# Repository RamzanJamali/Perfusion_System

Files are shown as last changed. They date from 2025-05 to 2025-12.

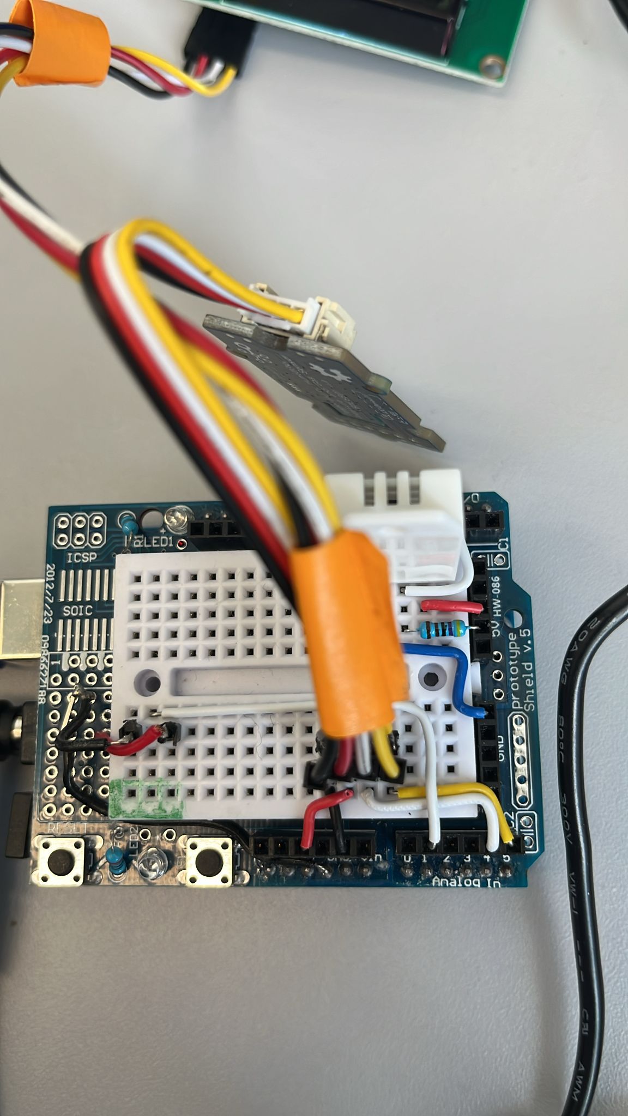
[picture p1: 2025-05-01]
Materials/SensorSetup.jpeg

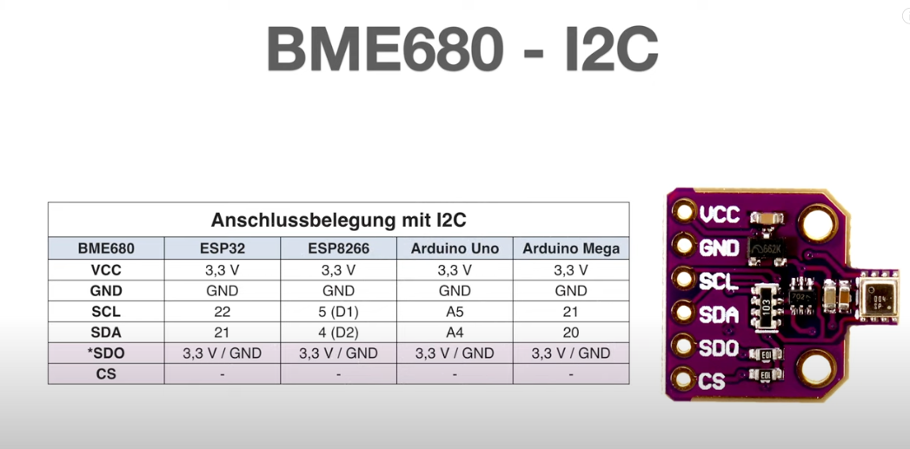
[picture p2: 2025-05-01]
Materials/Specs/BME680_I2C_specs.png

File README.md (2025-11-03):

# Pressure-Controlled Perfusion System

A modular, open-source pressure-controlled perfusion system designed for the biomechanical characterization of corneal tissue. This system provides precise control over retrocorneal pressure and perfusion flow rate for *ex vivo* experiments.

## 🚀 Quick Start

1.  **Hardware:** Assemble the mechanical components and connect the electronics as per the `hardware/` documentation.
2.  **Firmware:** Flash the Arduino with the appropriate controller firmware from the `Controller/` directory.
3.  **Software:** Install Python dependencies and run the recommended dashboard.
    ```bash
    pip install -r software/Dashboard_2/requirements.txt
    python software/Dashboard_2/app.py
    ```

## 📁 Repository Structure & Component Guide

Here is a breakdown of the key software components and their intended use:

| Component | Purpose | Recommendation |
| :--- | :--- | :--- |
| **`Controller/Controller_1`** | Firmware configured for the **Variohm CIT3100** pressure sensor. | Use if your hardware uses the CIT3100 sensor. |
| **`Controller/Controller_2`** | Firmware configured for the **Ceraphant PTC31B** pressure sensor. | **Recommended** for systems with the PTC31B sensor. |
| **`software/Dashboard_1`** | Legacy version of the Python control dashboard. | For reference or specific use cases. |
| **`software/Dashboard_2`** | Enhanced version with improved data visualization and control. | **Recommended** for all new installations. |

### 🔧 Hardware Specifications

Key components used in this system include:

*   **Stepper Motor Driver:** The TMC2209 driver module controls the NEMA 17 stepper motor, providing silent operation and advanced features like stealthChop2 for noiseless motion and spreadCycle for high-speed performance.
*   **Pressure Transducer:** The Ceraphant PTC31B is a pressure switch with a ceramic, vacuum-tight measuring cell, used for safe monitoring of absolute and gauge pressure. It is suitable for measurements in gases, vapors, and liquids.

## ⚙️ How to Use This Repository

### Downloading the Project

To get a copy of the project, you can **clone** the repository or **download it as a ZIP** file.

*   **Clone (recommended for development):**
    ```bash
    git clone https://github.com/RamzanJamali/Perfusion_System.git
    ```
*   **Download ZIP:**
    Click the `Code` button on the GitHub repository page and select "Download ZIP".

### Navigating the Code

- The `Controller/` directory contains the Arduino firmware. Select the version that matches your pressure sensor.
- The `software/` directory contains the Python-based dashboards. Use `Dashboard_2` for the best experience.
- Refer to the `hardware/` directory for assembly guides, CAD files, and the bill of materials.

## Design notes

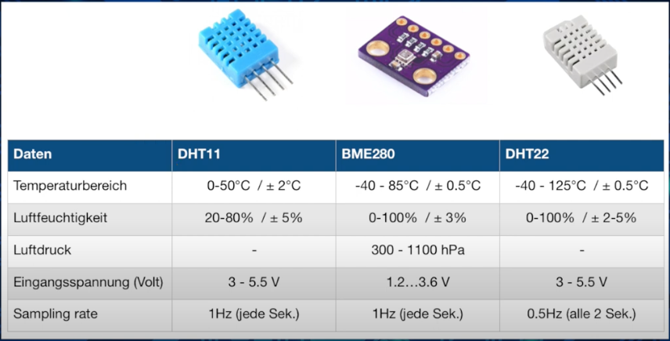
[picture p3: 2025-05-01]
Materials/Specs/DHT_specs.png

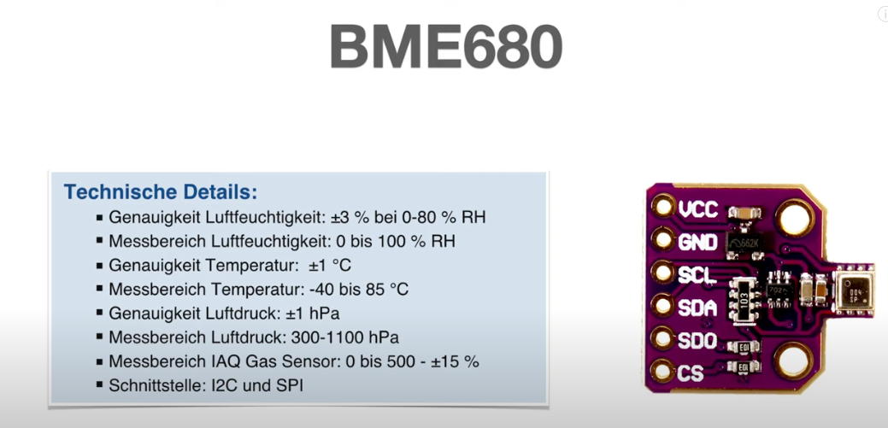
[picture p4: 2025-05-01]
Materials/Specs/BME680_specs.png

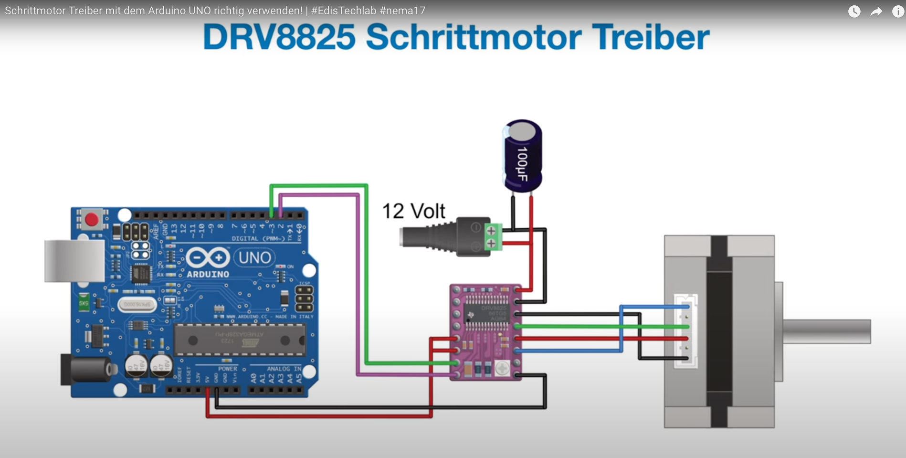
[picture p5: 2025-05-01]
Materials/Specs/DRV8825_motor_circuit.png

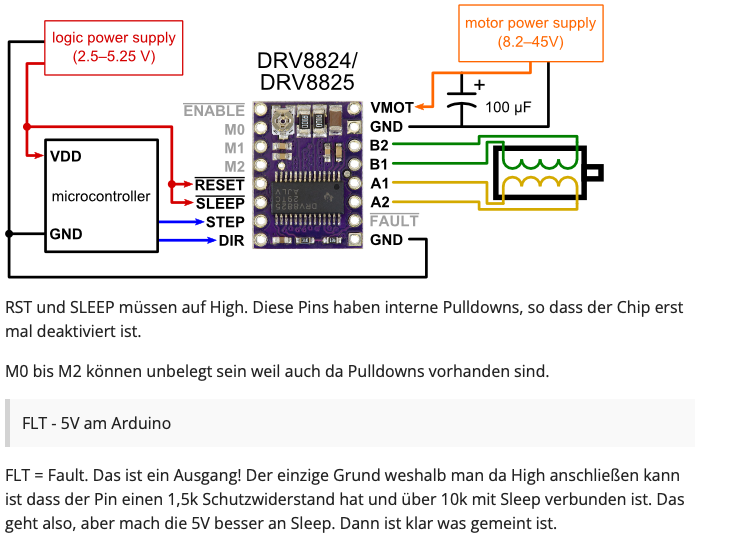
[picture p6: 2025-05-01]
Materials/Specs/DRV8825_circuit.png

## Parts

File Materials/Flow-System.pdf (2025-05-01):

## Etablierung eines druckkontrollierten

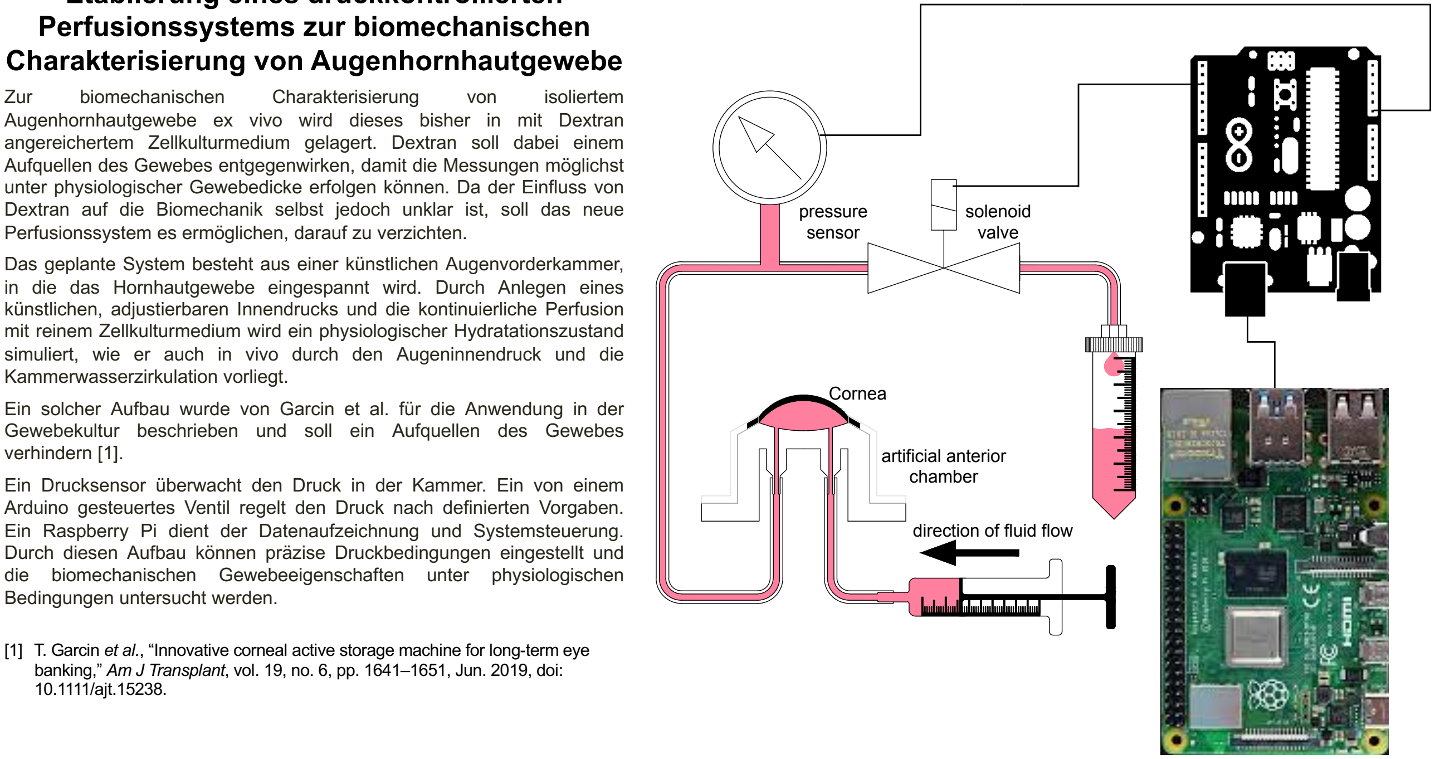
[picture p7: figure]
Perfusionssystems zur biomechanischen; Zur; biomechanischen; Charakterisierung; von; isoliertem; Kammerwasserzirkulation vorliegt.; verhindern [1].; die biomechanischen Gewebeeigenschaften unter physiologischen Bedingungen untersucht werden.; 10.1111/ajt.15238.; solenoid valve; pressure sensor; Cornea; artificial anterior chamber; direction of fluid flow

## Charakterisierung von Augenhornhautgewebe

Augenhornhautgewebe ex vivo wird dieses bisher in mit Dextran angereichertem Zellkulturmedium gelagert. Dextran soll dabei einem Aufquellen des Gewebes entgegenwirken, damit die Messungen möglichst unter physiologischer Gewebedicke erfolgen können. Da der Einfluss von Dextran auf die Biomechanik selbst jedoch unklar ist, soll das neue Perfusionssystem es ermöglichen, darauf zu verzichten.
Das geplante System besteht aus einer künstlichen Augenvorderkammer, in die das Hornhautgewebe eingespannt wird. Durch Anlegen eines künstlichen, adjustierbaren Innendrucks und die kontinuierliche Perfusion mit reinem Zellkulturmedium wird ein physiologischer Hydratationszustand simuliert, wie er auch in vivo durch den Augeninnendruck und die

Ein solcher Aufbau wurde von Garcin et al. für die Anwendung in der Gewebekultur beschrieben und soll ein Aufquellen des Gewebes

Ein Drucksensor überwacht den Druck in der Kammer. Ein von einem Arduino gesteuertes Ventil regelt den Druck nach definierten Vorgaben. Ein Raspberry Pi dient der Datenaufzeichnung und Systemsteuerung. Durch diesen Aufbau können präzise Druckbedingungen eingestellt und

[1] T. Garcin et al., “Innovative corneal active storage machine for long-term eye banking,” Am J Transplant, vol. 19, no. 6, pp. 1641–1651, Jun. 2019, doi:

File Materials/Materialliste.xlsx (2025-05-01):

Bauteil | Link | Bemerkung | Notiz
Netzteil
VOLTCRAFT VC-12878460 Steckernetzteil, Festspannung 24 V/DC 2.5 A 60 W | Conrad (https://www.conrad.de/de/p/voltcraft-vc-12878460-steckernetzteil-festspannung-24-v-dc-2-5-a-60-w-2575692.html) | 60 Watt
Schrittmotortreiber
Doppel H-Brücke DC Motor Controller Board Modul AZ-L298N | AZ-Delivery (https://www.az-delivery.de/products/dual-h-bridge-dc-motor-controller?gad_source=5) |  | Motor Spannung 5-35V / Logik Spannung 5-7V / Leistung 25 Watt / Maximalstrom pro Phase 4A / Dauerstrom pro Phase 2 A / 4 Phasen | Ich tendiere zum DRV 8825 habe allerdings keine Erfahrungen mit solchen Modulen und bin für Ratschläge dankbar
DRV8825 Schrittmotor-Treiber-Modul | AZ-Delivery (https://www.az-delivery.de/products/drv8825-schrittmotor-treiber-modul-mit-kuhlkorper?variant=37100118866&gad_source=5) | 5er set | Motor Spannung 8.2-45V / Logik Spannung intern 3.3V / Maximalstrom pro Phase 2,5A / Dauerstrom pro Phase 1 A / Schritte: Voll, 1/2, 1/4, 1/8, 1,16, und 1/32 / 4 Phasen
Sensoren
DHT22 AM2302 Temperatursensor und Luftfeuchtigkeitssensor | AZ-Delivery (https://www.az-delivery.de/products/dht22?_pos=1&_sid=f178b3009&_ss=r)
101020513 - BME680 Temperatur-, Feuchtigkeits- und Drucksensor für Arduino | Distrelec (https://www.distrelec.de/de/bme680-temperatur-feuchtigkeits-und-drucksensor-fuer-arduino-seeed-studio-101020513/p/30121569?ext_cid=gpgooaqdede-Search-DSACatch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)
Variohm CIT3100-G-00004-B-4-A | Variohm (https://www.variohm.de/produkte/drucksensoren-und-druckschalter/drucksensoren/cit3100-niederdrucksensoren)
Ceraphant PTC31B-AAAM1CGBWBJA | Endress & Hauser (https://www.de.endress.com/de/messgeraete-fuer-die-prozesstechnik/druck/Absolut-Relativ-Ceraphant-PTC31B?t.tabId=product-configure)
Schrittmotor:
Joy-it Schrittmotor NEMA17-06 neu 0.59 Nm 2 A 2 A Wellen-Durchmesser: 5 mm | Conrad (https://www.conrad.de/de/p/joy-it-schrittmotor-nema17-06-neu-0-59-nm-2-a-2-a-wellen-durchmesser-5-mm-2355876.html)
Sonstiges
MB102 Breadboard Netzteil Adapter Power Supply Modul 3.3V/5V | AZ-Delivery (https://www.az-delivery.de/products/mb102-breadboard?_pos=45&_sid=0396cc324&_ss=r) | 3er Set | Prototyping Adapter um die Schaltungen zu testen könnte gut sein um die Schrittmotorschaltung anfangs zu testen
ElKo Sortiment Elektrolytkondensator Aluminium 24 Varianten, 500 Stück 0.1uF – 1000uF | AZ-Delivery (https://www.az-delivery.de/products/elko-sortiment-mit-500-stuck-elektrolytkondensatoren-0-1-f-1000-f) |  | Für den Betrieb eines DRV 8825 wird ein Kondensator (100 µF) benötigt
Prototyping Prototype Shield Mini Breadboard für UNO R3 | AZ-Delivery (https://www.az-delivery.de/products/prototyping-shield?variant=6127218851867) | 5er Set
1-Relais 5V KY-019 Modul High-Level-Trigger | AZ-Delivery (https://www.az-delivery.de/products/relais-modul?variant=8138392109152) | 5er Set | Steuerung des Magnetventiels (Stomschalter)
Hochpräzises Strom-zu-Spannungswandler Modul, 4-20mA auf 0-5V Signalumwandlungsmodul I/V-Wandler Analogausgang Platine | Amazon (https://www.amazon.de/Strom-zu-Spannungswandler-Signalumwandlungsmodul-Konverter-Analogausgang-Board/dp/B07XNPLQ3K?__mk_de_DE=ÅMÅŽÕÑ&nsdOptOutParam=true&s=ce-de) |  | Amazon wurde von meinem Endress und Hauser Kontakt empfohlen fruugo ist günstiger aber auch anders und eventuell komplizierter zum Einstellen
Current To Voltage Module 0/4-20mA To 0-3.3V 5V 10V Voltage Transmitter | fruugo (https://www.fruugo.de/strom-zu-spannungs-modul-04-20ma-bis-0-33v-5v-10v-spannungstransmitter/p-274529440-609483705?language=de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)
LCD Display
HD44780 2004 LCD Display Bundle 4x20 Zeichen mit I2C Schnittstelle | AZ-Delivery (https://www.az-delivery.de/products/hd44780-2004-lcd-display-bundle-4x20-zeichen-mit-i2c-schnittstelle?variant=13538165915744) | 3er Set | Sind noch zwei in Freiburg vorrätig
Mechanische Bauteile
Wellenkupplung RB flexibel D18L25 5,00/6,35mm | dold (https://www.dold-mechatronik.de/Wellenkupplung-RB-flexibel-D18L25-500-635mm)
Linearlager 8mm LM8UUAJ, einstellbar | dold (https://www.dold-mechatronik.de/Linearlager-8mm-LM8UUAJ-einstellbar)
Präzisionswelle 8mm h6, geschliffen und gehärtet, Edelstahl X46Cr13 (1.4034), 0,4kg/m, Zuschnitt 50-3000mm | dold (https://www.dold-mechatronik.de/Praezisionswelle-8mm-h6-geschliffen-und-gehaertet-Edelstahl-X46Cr13-Zuschnitt) | 2 x 1000 mm
1 Gewindestange M8x1000 mm - Edelstahl A4 - DIN 976 | BefestigungsFuchs (https://www.befestigungsfuchs.de/eisenwaren/gewindestangen-gewindestuecke/edelstahl/1-gewindestange-m8x1000-mm-edelstahl-a4-din-976) | 2 x 1000 mm
40tlg Muttern/Unterlegscheiben Set für M8 Gewindestangen Edelstahl A4 | BefestigungsFuchs (https://www.befestigungsfuchs.de/eisenwaren/gewindestangen-gewindestuecke/edelstahl/40tlg-muttern-unterlegscheiben-set-fuer-m8-gewindestangen-edelstahl-a4)
1 Zylinderschraube M3x14mm - Innensechskant - Edelstahl A4 - DIN 7984 | BefestigungsFuchs (https://www.befestigungsfuchs.de/schrauben/zylinderschrauben/innensechskant/1-zylinderschraube-m3x14mm-innensechskant-edelstahl-a4-din-7984) | 40 Stk bestellen für Mengenrabatt
1 Sechskantmutter - M3 - SW5.5 - Edelstahl A4-50 - DIN 934 | BefestigungsFuchs (https://www.befestigungsfuchs.de/eisenwaren/muttern/sechskantmuttern/1-sechskantmutter-m3-sw5.5-edelstahl-a4-50-din-934) | 20 Stk bestellen für Mengenrabatt
1 Unterlegscheibe DIN 125 Form A - für M3 - Aussen-Ø=7mm - Edelstahl A2 | BefestigungsFuchs (https://www.befestigungsfuchs.de/eisenwaren/unterlegscheiben-ringe/1-unterlegscheibe-din-125-form-a-fuer-m3-aussen-oe-7mm-edelstahl-a2) | 20 Stk bestellen für Mengenrabatt
500 Innensechskantschrauben mit Teilgewinde DIN 912 Edelstahl A4 5x8mm | Befestigungsfuchs (https://www.befestigungsfuchs.de/schrauben/zylinderschrauben/innensechskant/500-innensechskantschrauben-mit-teilgewinde-din-912-edelstahl-a4-5x8mm)
0.0.448.07 -- / -- Profil 5 20x40 natur 3.000mm | ITEM (https://www.item24.com/de-de/profil-5-40x20-natur-44807?supplyUnit=STUECK&nominalLength=3000&nuten=-1&category=profiltechnik)

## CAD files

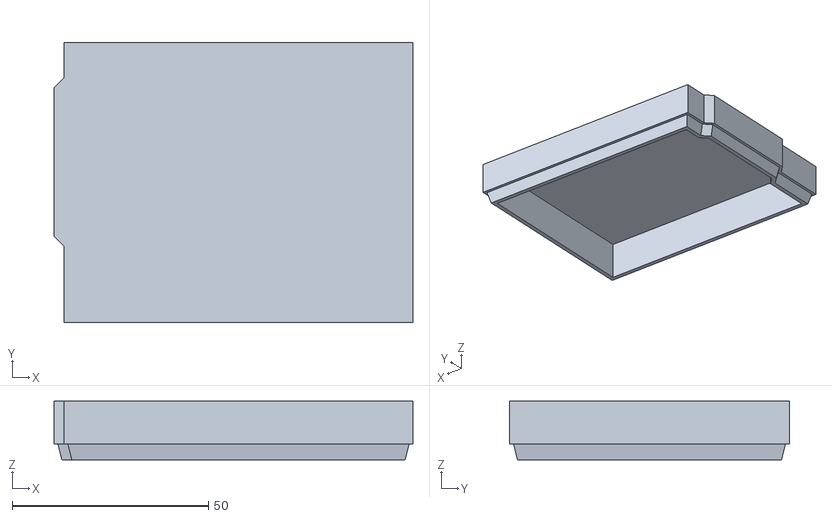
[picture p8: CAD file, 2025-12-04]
3D files/Arduino_Housing Top v2.stl
91.6 x 71.3 x 15.0

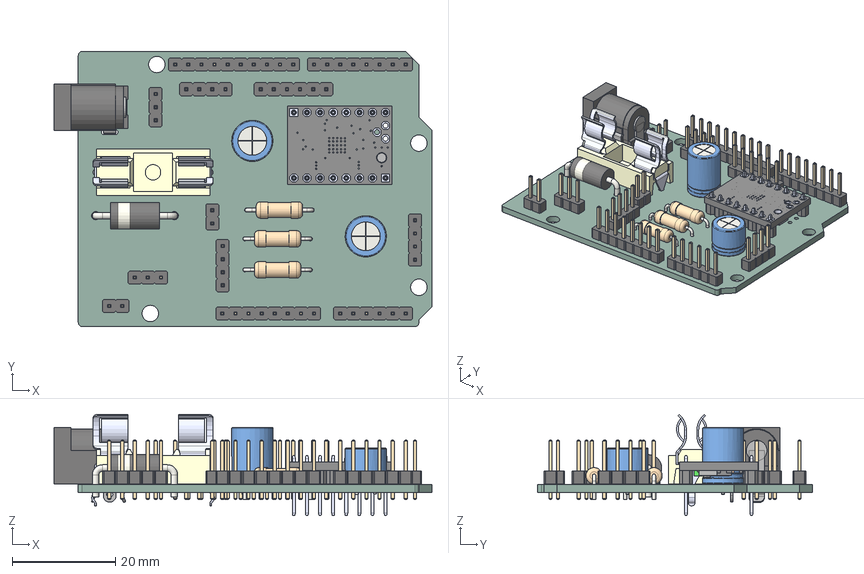
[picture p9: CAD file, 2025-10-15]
Perfusion_Shield/Perfusion_Shield.step
73.3 x 53.3 x 19.6 mm
PinHeader_1x08_P2.54mm_Vertical x 2
PinHeader_1x06_P2.54mm_Vertical x 2
PinHeader_1x10_P2.54mm_Vertical
PinHeader_1x03_P2.54mm_Vertical x 2
MC000827
PinHeader_1x04_P2.54mm_Vertical x 3
R_Axial_DIN0309_L9.0mm_D3.2mm_P12.70mm_Horizontal x 3
PinHeader_1x02_P2.54mm_Vertical x 2
C_Radial_D8.0mm_H7.0mm_P3.50mm
BarrelJack_GCT_DCJ200-10-A_Horizontal
D_DO-201AD_P15.24mm_Horizontal
TMC2209SILENTSTEPSTICK--3DModel-STEP-269445
C_Radial_D8.0mm_H11.5mm_P3.50mm
Perfusion_Shield_PCB

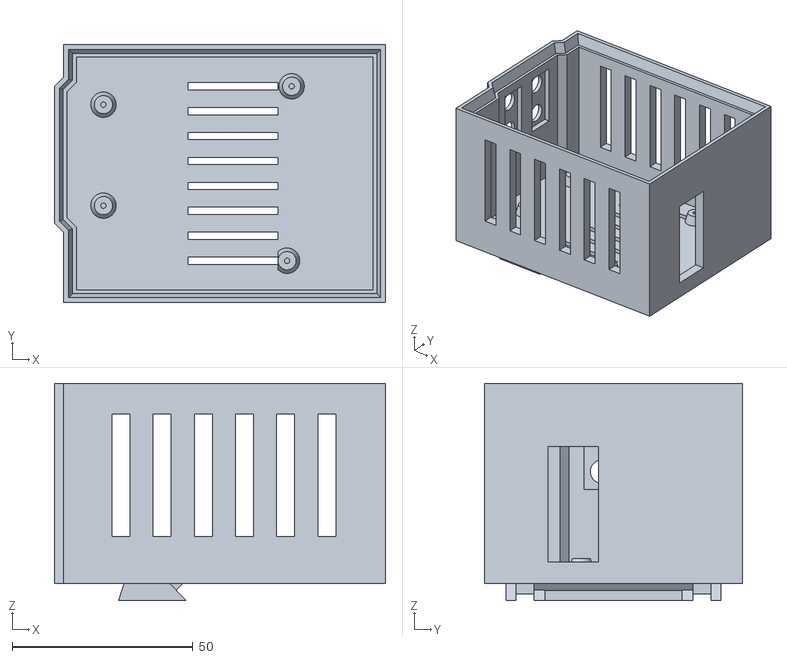
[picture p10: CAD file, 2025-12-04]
3D files/Arduino_Housing v5.stl
91.6 x 71.3 x 60.1

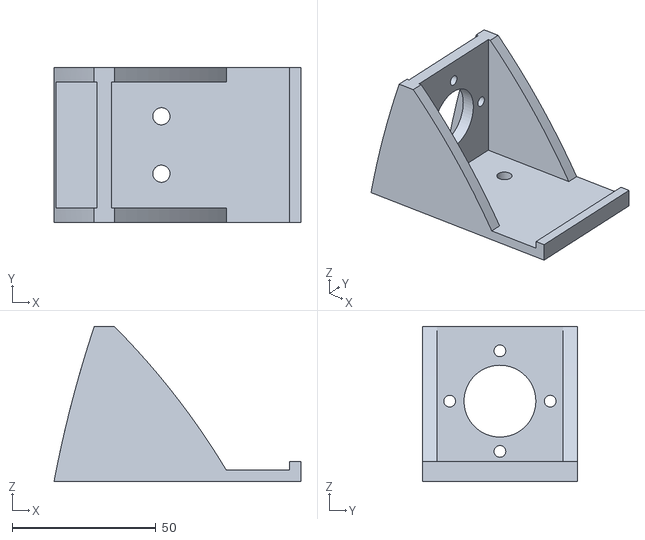
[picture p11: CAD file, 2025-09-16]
3D files/MGL17-G20_Holder v1.stl
86.0 x 54.0 x 54.0

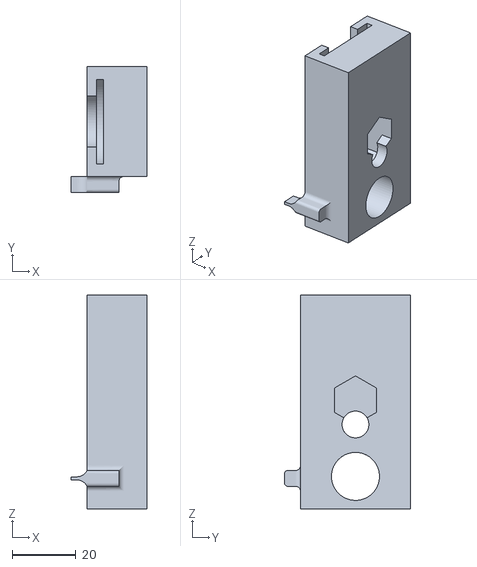
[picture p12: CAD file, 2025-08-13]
3D files/Plunger v15.stl
23.8 x 39.5 x 67.1

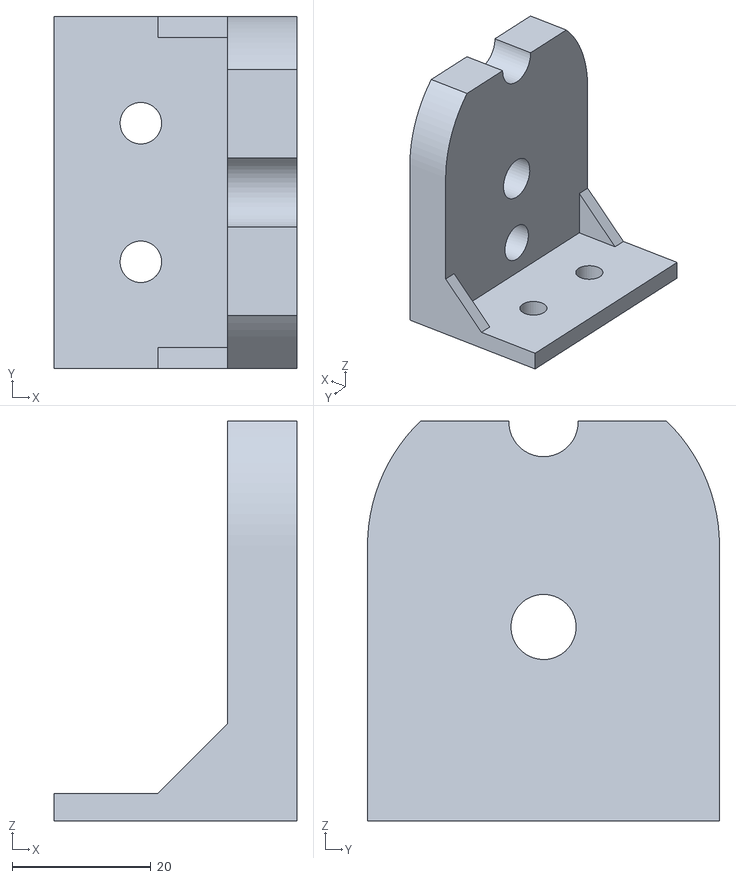
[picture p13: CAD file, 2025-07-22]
3D files/Syringe_10ml v7.stl
35.0 x 50.8 x 57.7

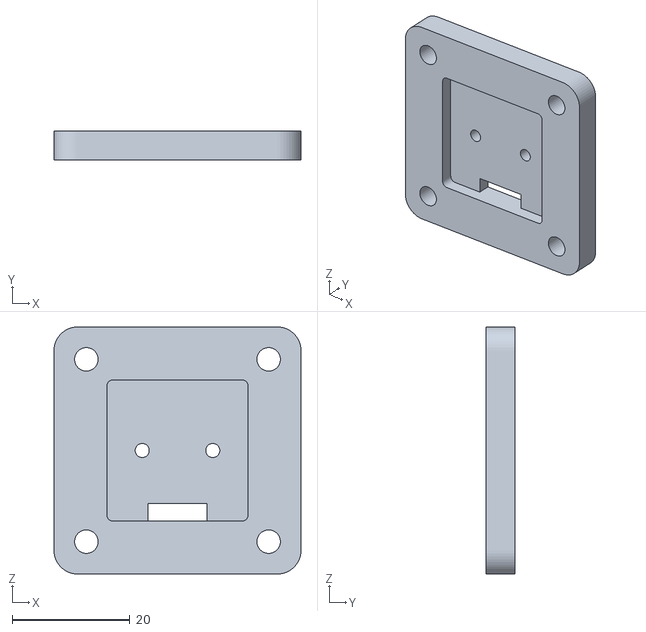
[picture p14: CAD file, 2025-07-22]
3D files/AS5048A_mount v2.stl
42.0 x 5.00 x 42.0

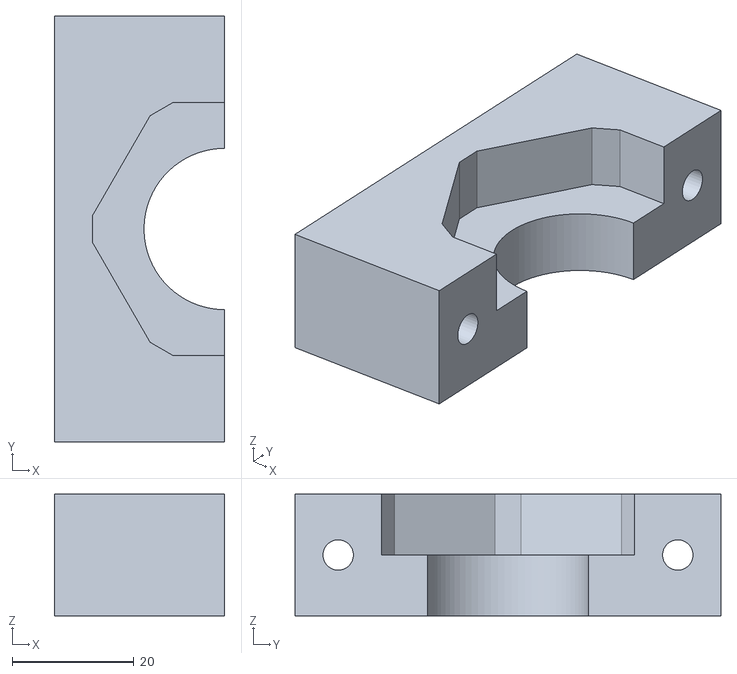
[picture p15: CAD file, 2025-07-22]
3D files/Pressure_Sensor_Holder v3.stl
28.0 x 70.0 x 20.0

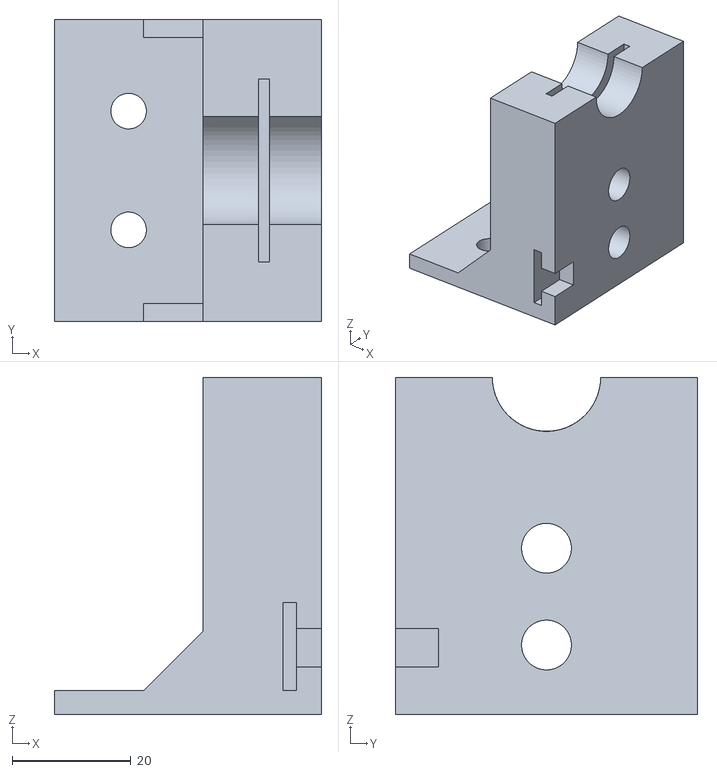
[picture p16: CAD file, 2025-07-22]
3D files/Barrel 10ml with IR Button v3.stl
45.0 x 50.8 x 56.8

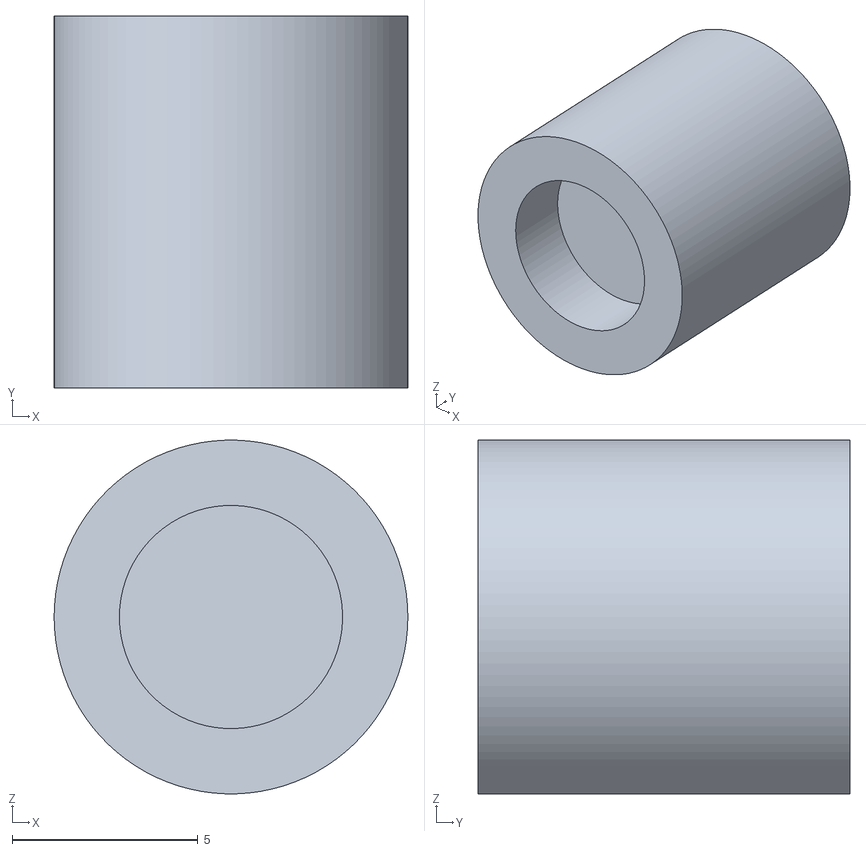
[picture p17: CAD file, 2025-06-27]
3D files/Magnet_holder v2.stl
9.51 x 10.0 x 9.50

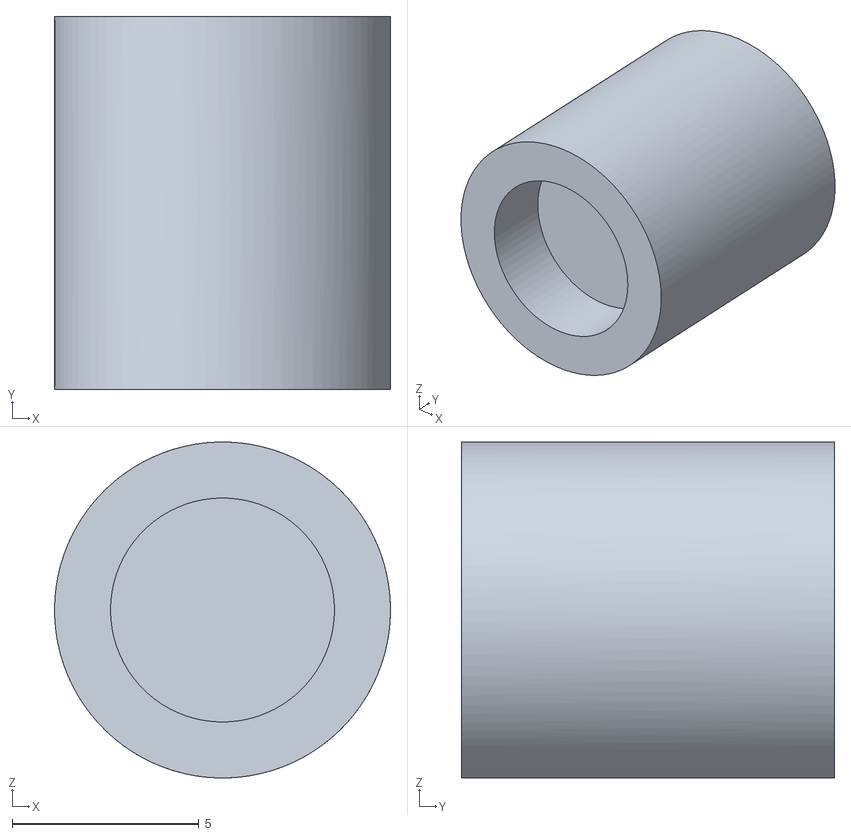
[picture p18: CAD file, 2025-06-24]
3D files/Magnet_holder v1.stl
9.00 x 10.0 x 9.00

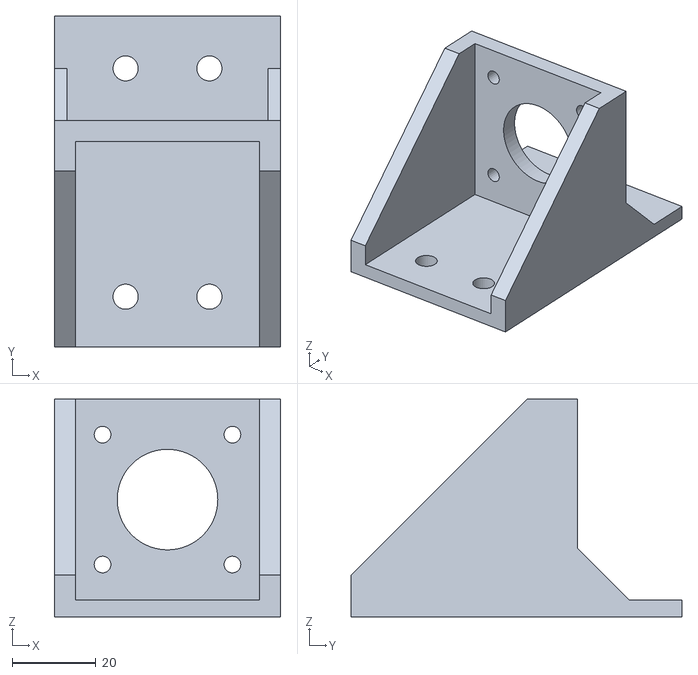
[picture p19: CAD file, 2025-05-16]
3D files/NemaMount 2 v3.stl
54.0 x 79.0 x 52.0

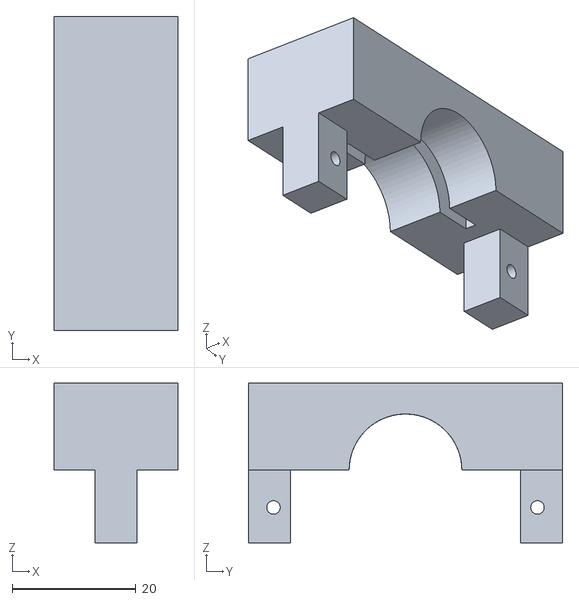
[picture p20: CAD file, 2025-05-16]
3D files/Barrel_head.stl
20.0 x 50.8 x 25.9

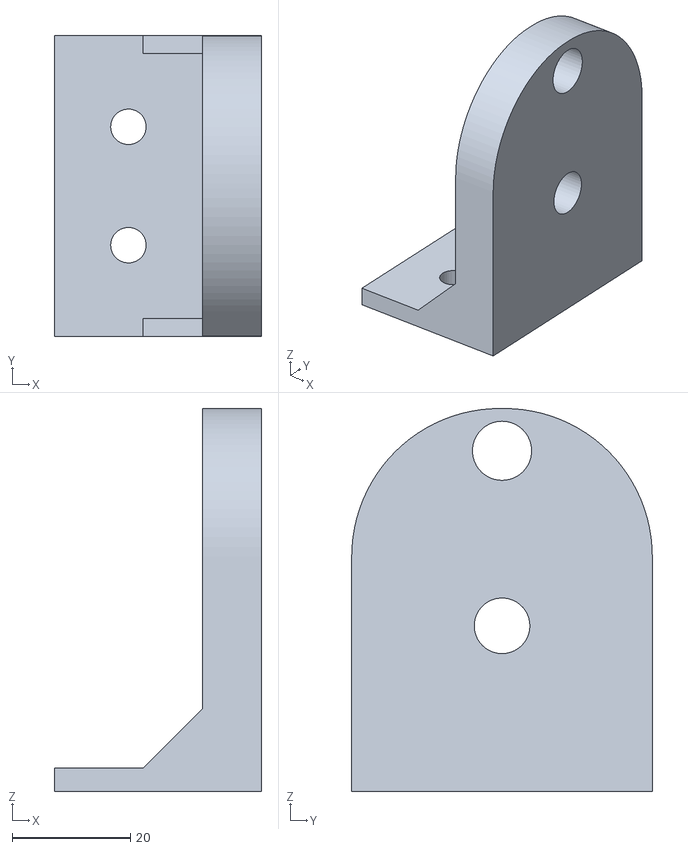
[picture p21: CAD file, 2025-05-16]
3D files/Syringe_10ml v5.stl
35.0 x 50.8 x 64.7

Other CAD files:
3D files/Barrel 10ml with IR Button v2.stl
3D files/AS5048A_mount v1.stl
3D files/Barrel_Body.stl
3D files/Arduino base v12.step
3D files/AS5048A_mount v1.ipt
3D files/AS5048A_mount v2.ipt
3D files/Arduino base v12.ipt
3D files/Arduino base v12.stl
3D files/Arduino_Housing Top.ipt
3D files/Arduino_Housing v5.ipt
3D files/Barrel 10ml v6.ipt
3D files/Barrel 10ml with IR Button v2.ipt
3D files/Barrel 10ml with IR Button v3.ipt
3D files/Barrel v11.ipt
3D files/Barrel v11.step
3D files/MGL17-G20_Holder v1.ipt
3D files/Magnet_holder v0.ipt
3D files/Magnet_holder v2.ipt
3D files/NemaMount v9.ipt
3D files/NemaMount v9.step
3D files/NemaMount_2 v3.ipt
3D files/Perfusion_Shield v35.f3z
3D files/Plunger v14.ipt
3D files/Plunger v14.step
3D files/Plunger v14.stl
3D files/Plunger v15.ipt
3D files/Pressure_Sensor_Holder v3.ipt
3D files/Syringe v11.ipt
3D files/Syringe v11.step
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

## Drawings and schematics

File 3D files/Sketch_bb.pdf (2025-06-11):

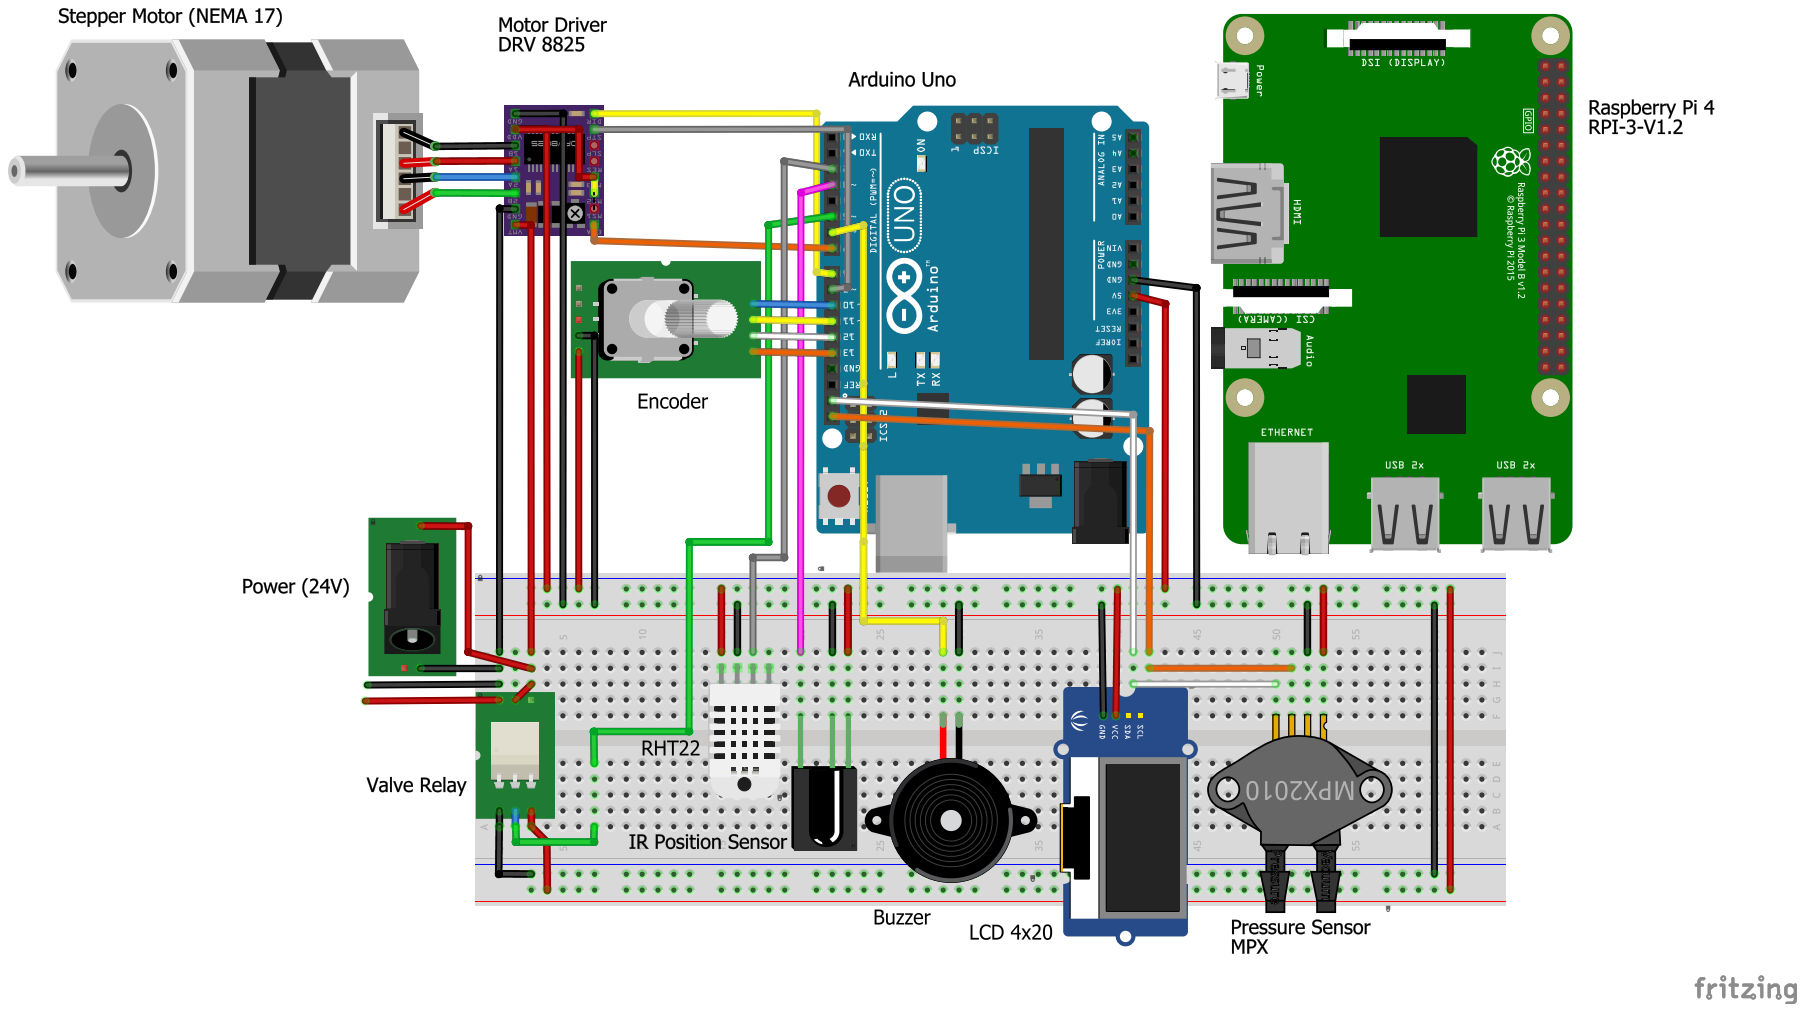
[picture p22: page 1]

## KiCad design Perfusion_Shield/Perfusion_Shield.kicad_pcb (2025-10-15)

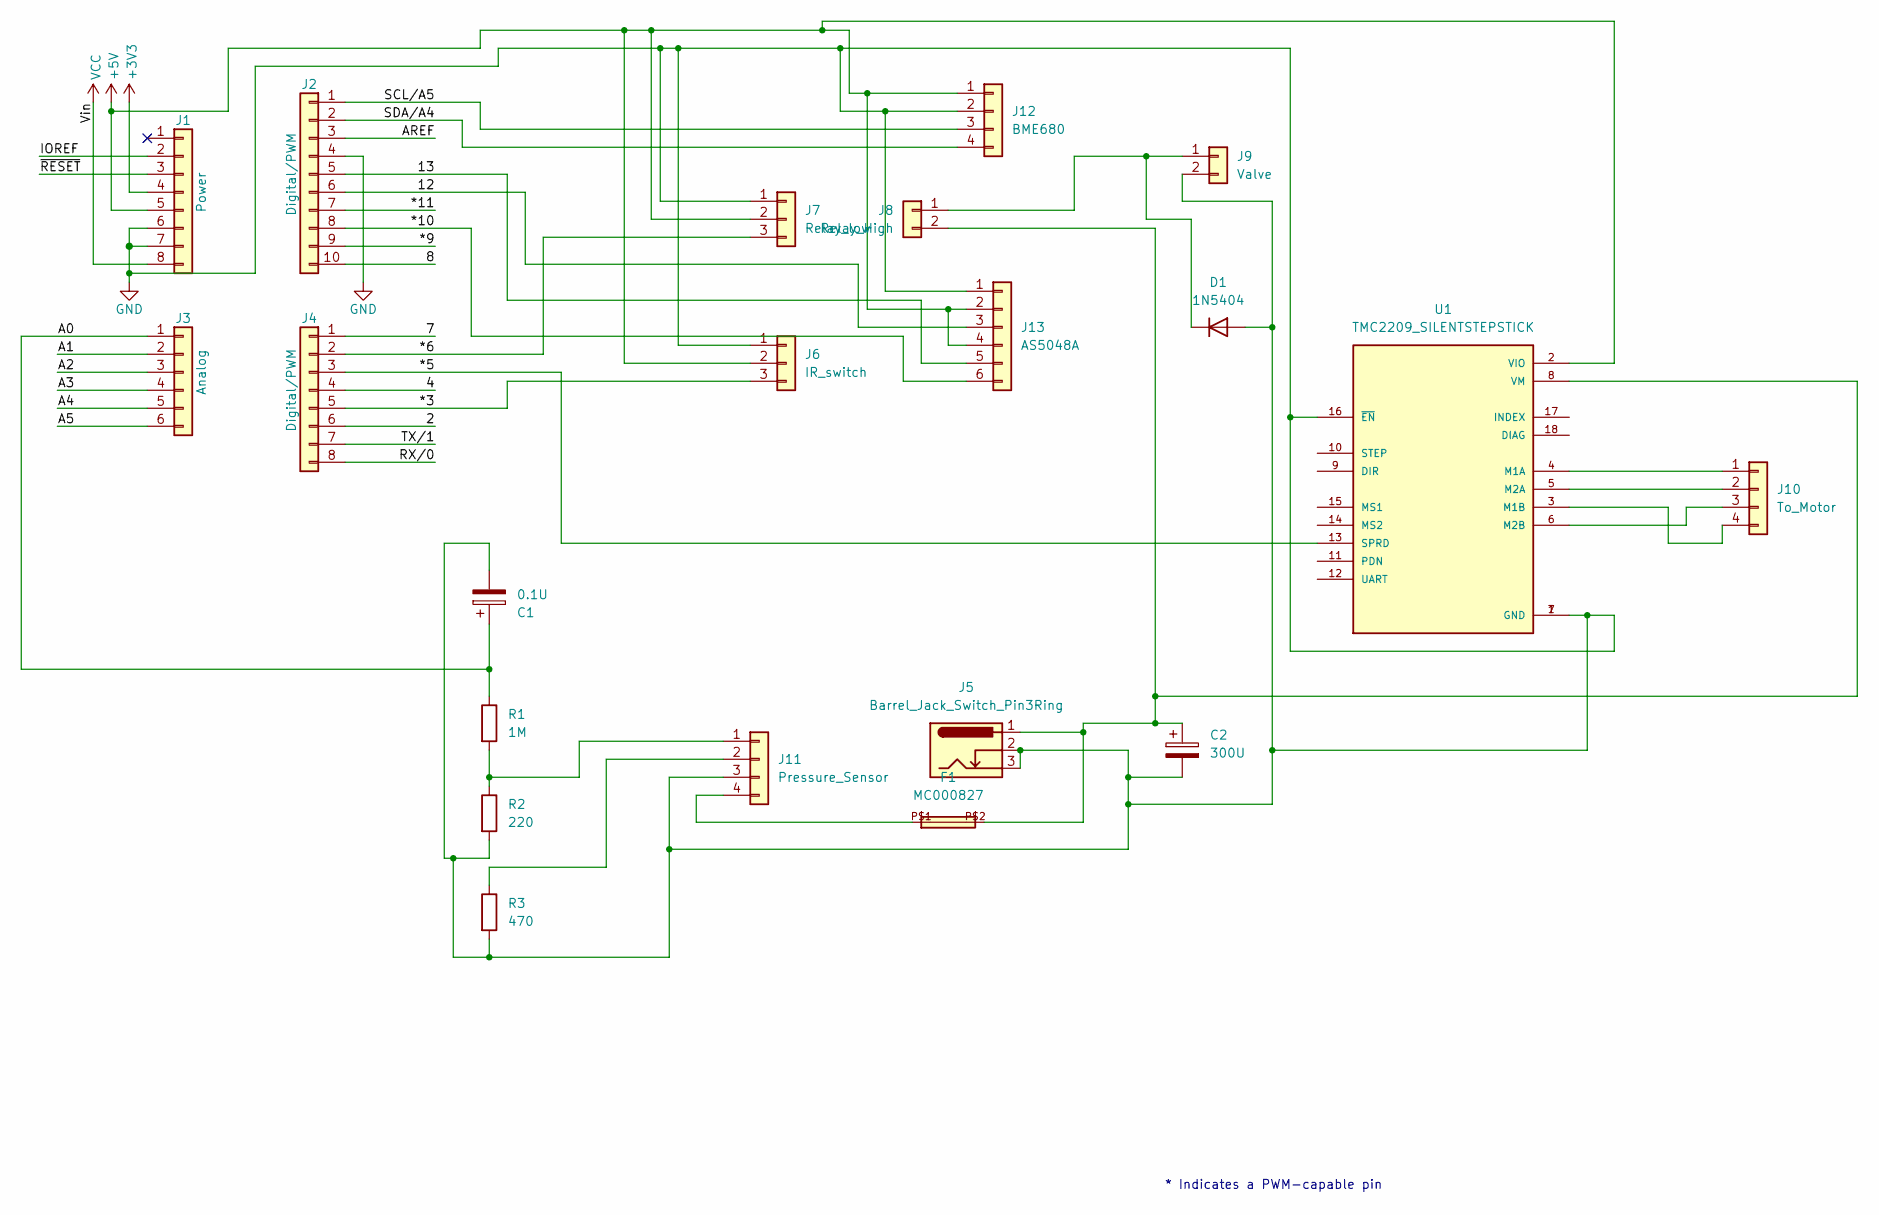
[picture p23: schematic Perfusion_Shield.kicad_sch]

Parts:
C1: 0.1U; C_Radial_D8.0mm_H7.0mm_P3.50mm
C2: 300U; C_Radial_D8.0mm_H11.5mm_P3.50mm
D1: 1N5404; D_DO-201AD_P15.24mm_Horizontal
F1: MC000827
J1: Power; PinHeader_1x08_P2.54mm_Vertical
J2: Digital/PWM; PinHeader_1x10_P2.54mm_Vertical
J3: Analog; PinHeader_1x06_P2.54mm_Vertical
J4: Digital/PWM; PinHeader_1x08_P2.54mm_Vertical
J5: Barrel_Jack_Switch_Pin3Ring; BarrelJack_GCT_DCJ200-10-A_Horizontal
J6: IR_switch; JST_XH_B3B-XH-A_1x03_P2.50mm_Vertical
J7: Relay_low; JST_XH_B3B-XH-A_1x03_P2.50mm_Vertical
J8: Relay_High; JST_XH_B2B-XH-A_1x02_P2.50mm_Vertical
J9: Valve; JST_XH_B2B-XH-A_1x02_P2.50mm_Vertical
J10: To_Motor; JST_XH_B4B-XH-A_1x04_P2.50mm_Vertical
J11: Pressure_Sensor; JST_XH_B4B-XH-A_1x04_P2.50mm_Vertical
J12: BME680; JST_XH_B4B-XH-A_1x04_P2.50mm_Vertical
J13: AS5048A; JST_XH_B6B-XH-A_1x06_P2.50mm_Vertical
R1: 1M; R_Axial_DIN0309_L9.0mm_D3.2mm_P12.70mm_Horizontal
R2: 220; R_Axial_DIN0309_L9.0mm_D3.2mm_P12.70mm_Horizontal
R3: 470; R_Axial_DIN0309_L9.0mm_D3.2mm_P12.70mm_Horizontal
U1: TMC2209_SILENTSTEPSTICK; MODULE_TMC2209_SILENTSTEPSTICK; PARTREV 1.20

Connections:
+3V3: J1.4
+5V: J1.5, J6.2, J7.2, J12.1, J13.2, J13.4, U1.2 (VIO)
/2: J4.6
/4: J4.4
/7: J4.1
/8: J2.10
/12: J2.6, J13.3
/13: J2.5, J13.5
/*3: J4.5, J6.3
/*5: J4.3, U1.13 (SPRD)
/*6: J4.2, J7.3
/*9: J2.9
/*10: J2.8, J13.6
/*11: J2.7
/A0: C1.1, J3.1, R1.1
/A1: J3.2
/A2: J3.3
/A3: J3.4
/A4: J3.5
/A5: J3.6
/AREF: J2.3
/IOREF: J1.2
/RX/0: J4.8
/SCL/A5: J2.1, J12.3
/SDA/A4: J2.2, J12.4
/TX/1: J4.7
/~RESET: J1.3
GND: C1.2, C2.2, D1.2 (A), J1.6, J1.7, J2.4, J5.2, J5.3, J6.1, J7.1, J9.2, J11.3, J12.2, J13.1, R2.2, R3.2, U1.1 (GND), U1.7 (GND), U1.16 (~EN)
unnamed: D1.1 (K), J8.1, J9.1
unnamed: C2.1, F1.P$2, J5.1, J8.2, U1.8 (VM)
unnamed: J10.1, U1.4 (M1A)
unnamed: J10.2, U1.5 (M2A)
unnamed: J10.3, U1.6 (M2B)
unnamed: J10.4, U1.3 (M1B)
unnamed: J11.1, R1.2, R2.1
unnamed: J11.2, R3.1
unnamed: F1.P$1, J11.4
VCC: J1.8

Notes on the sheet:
* Indicates a PWM-capable pin

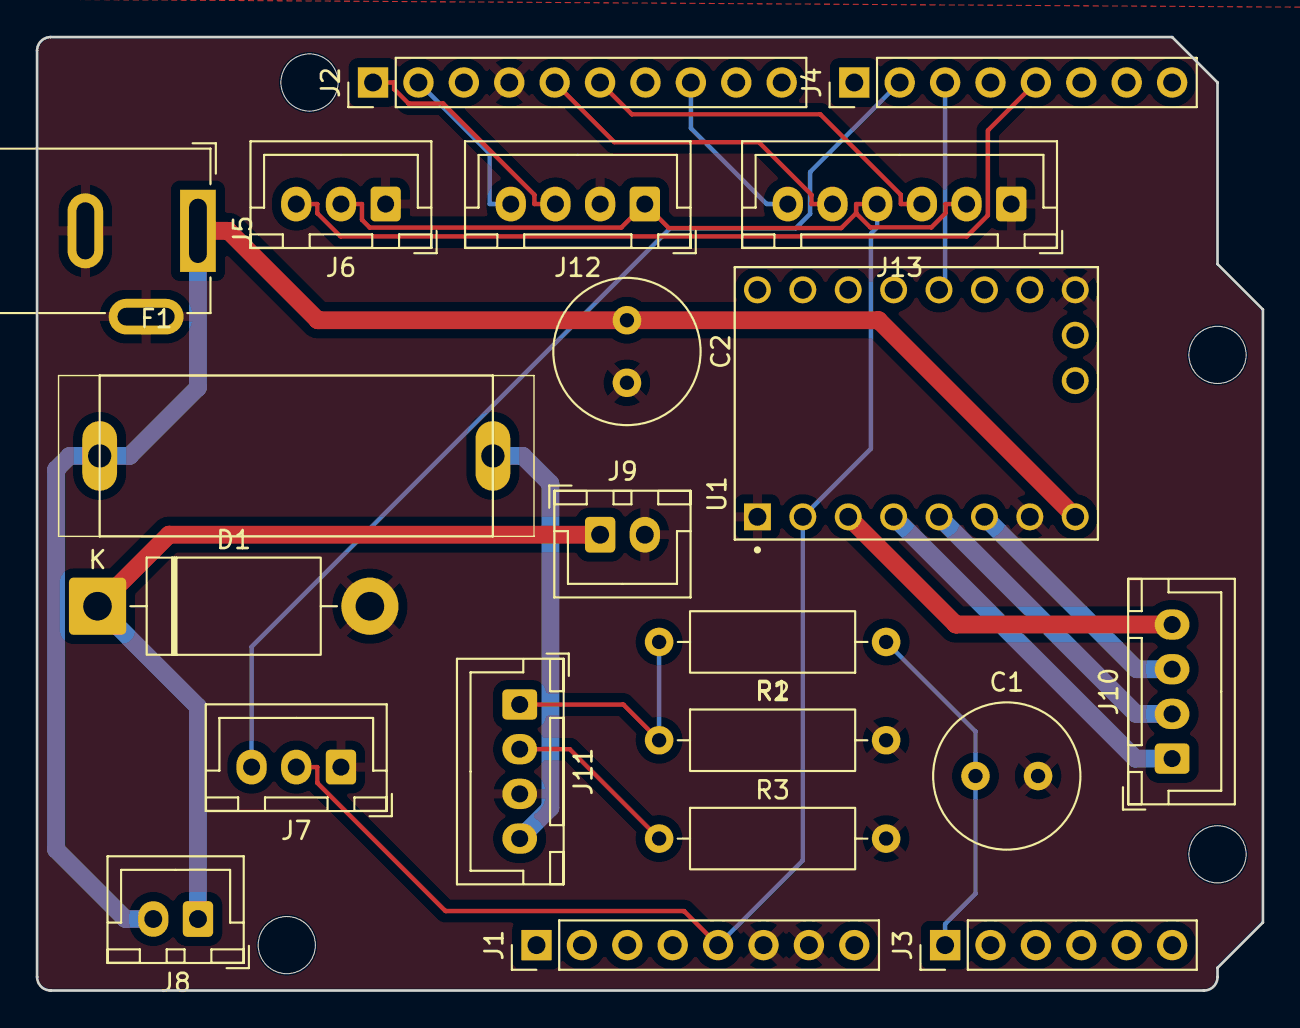
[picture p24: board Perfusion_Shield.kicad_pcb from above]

Board: 2 copper layers, 68.6 x 53.3 mm, 25 parts (0 on the bottom side), 20 nets.

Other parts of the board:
MH1, MH2, MH3, MH4: MountingHole_3.2mm

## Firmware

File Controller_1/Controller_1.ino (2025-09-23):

#include "config.h"
#include "TMC.h"
#include "AS5048A.h"
#include "Pressure.h"
#include "PERFUSION.h"
//#include "ReadTemperatureHumidity.h"

#include <Wire.h>
#include <Adafruit_Sensor.h>
#include "Adafruit_BME680.h"


Adafruit_BME680 bme; // I2C

bool at_end_position = LOW; //define a numeric variable


float desired_flow_rate = 0;
float target_pressure = 15;
int runCurrentPercent = 100;
static double rpm = 0;
float abs_time;

bool valve_status = false;
// define our CS PIN 
AS5048A ABS(CS_PIN);

// Initialize variables for pressure sensor
int raw_pressure = 0;         // Variable to store raw sensor reading
static int raw_low = 0;               // low raw sensor reading
static int raw_high = 0;              // high raw sensor reading

// Create perfusion system
Perfusion perfusion(VALVE_PIN, target_pressure); // 
TMC_DRIVER tmc_driver(RX_PIN, TX_PIN, runCurrentPercent);

// commands for arduino to operate. 
String inputString = "";
const char delimiter = ',';
const int maxCommands = 6;
String Commands[maxCommands] = {"IDLE", "500", "2.5", "0", "0", "0"}; // {perfusion_state, pressure, flow_rate, raw_low, raw_high}

String result;
//String data[] = {"1", "90", "45", "45", "45", "2", "CW"}; // Pressure, tilt, gyro x, gyro y, gyro z, Motor Speed, Motor Direction


static uint32_t prev_time = 0;
static uint32_t abs_prev_time = 0;

void setup() {

	Serial.begin(115200);
	//Serial.setTimeout(500);
	perfusion.set_end_position(0); // Set syringe end position
	tmc_driver.begin();

	// BME sensor setup
	bme_setup();

	//pinMode(LED_PIN, OUTPUT);
	pinMode(BUTTON_PIN, INPUT);
	
	// For AS5048A encoder
  pinMode(CS_PIN, OUTPUT);
  digitalWrite(CS_PIN, HIGH);

	ABS.SPI_setup();
	ABS.update_info();


	Serial.println("<OK>");

}

void loop() {
	
  if (perfusion.get_valve_state() == HIGH){
        valve_status = true;
      }
	result = ReadTemperatureHumidity();

  raw_pressure = analogRead(PRESSURE_PIN);
  if (raw_low == 0 || raw_high == 0) {
    perfusion.set_current_pressure(raw_pressure);
  }
  else {
    perfusion.set_current_pressure(Pressure(LOW_PRESSURE, HIGH_PRESSURE, raw_low, raw_high, raw_pressure));
  }

	
	if (Serial.available()) {
		inputString = Serial.readStringUntil('\n'); // Read until newline
		inputString.trim();
		//Serial.println(inputString);
		
		if (inputString != Commands[0]+","+Commands[1]+","+Commands[2]+","+Commands[3]+","+Commands[4]+","+Commands[5]) {
			CommandParser(inputString, Commands);
			//Status();
			//Serial.println("<"+Commands[0]+","+Commands[1]+">");
		}
		else{
			//Status();
		}
		
	}

	//for (int x = 0; x<7; x++){
			//Serial.print(Commands[x]);
	//		}
	
	// In next step, these all if conditions will be put in a separate file in a function and only the function will be called here.
	if (Commands[0] == "START_PERFUSION") {
			
      if (perfusion.get_valve_state() == HIGH){
        valve_status = true;
      }
			if (perfusion.get_end_position() == HIGH){
				tmc_driver.stop();
        perfusion.end_perfusion();
			}
			else {
				perfusion.start_perfusion();
				tmc_driver.run();
			}


	} else if (Commands[0] == "PAUSE_PERFUSION") {
		  perfusion.pause_perfusion();
			tmc_driver.stop();
      

	} else if (Commands[0] == "CONTINUE_PERFUSION"){
			
      if (perfusion.get_valve_state() == 1){
        valve_status = true;
      }
			if (perfusion.get_end_position() == HIGH){
				tmc_driver.stop();
        perfusion.end_perfusion();
			}
			else {
				perfusion.start_perfusion();
				tmc_driver.run();
			}


	} else if (Commands[0] == "END_PERFUSION") {
		  perfusion.end_perfusion();
			tmc_driver.stop();
	} else {
		}

	// Secondary commands
	if (Commands[1] != "1"){
		perfusion.set_target_pressure(Commands[1].toFloat());
	} else {}

	if(Commands[2].toFloat() != desired_flow_rate){
		desired_flow_rate = Commands[2].toFloat();
		tmc_driver.flow_rate(desired_flow_rate);
	} 
	else {
		}
	if (desired_flow_rate < -1 && perfusion.get_state() == 0) {
		tmc_driver.run();
	}
	else if (perfusion.get_state() == 0) {
		tmc_driver.stop();
	}


	if ((Commands[3].toFloat() != -1) && perfusion.get_state() == 0) {
			raw_low = Commands[3].toFloat();
	}

	if ((Commands[4].toFloat() != -1) && perfusion.get_state() == 0) {
		raw_high = Commands[4].toFloat();
	}
	
	if (perfusion.get_state() == 0) {
		if (Commands[5].toInt() == 1) {
    	if (perfusion.get_valve_state() == 0){
      perfusion.opened_valve();
      
      } else {}

		} else if (Commands[5].toInt() == 0){
			perfusion.closed_valve();
		} else {}
	}

  raw_pressure = analogRead(PRESSURE_PIN);
	if (raw_low == 0 || raw_high == 0) {
		perfusion.set_current_pressure(raw_pressure);
	}
	else {
		perfusion.set_current_pressure(Pressure(LOW_PRESSURE, HIGH_PRESSURE, raw_low, raw_high, raw_pressure));
	}
  


if (desired_flow_rate != 0 ){
  abs_time = 25000 / abs(desired_flow_rate);
}
else {
  abs_time = 10000;
}

  uint32_t abs_current_time = millis();
  if (abs_current_time - abs_prev_time >= abs_time) {
    ABS.update_info();
    rpm = ABS.get_speed();
    
    abs_prev_time = abs_current_time;
  }

  if (perfusion.get_valve_state() == HIGH){
        valve_status = true;
      }
	uint32_t current_time = millis();
	if (current_time - prev_time > 990) { 
	  Status();
		if (perfusion.get_state() == 1) {
			valve_status = perfusion.get_valve_state();
		}
		prev_time = current_time;
	}


	//perfusion.update_data(data);
	//delay(999);
	//Status();


 float a = perfusion.get_current_pressure();
 float b = perfusion.get_target_pressure();
 b = b * 1.3;


 if (a > b) {
    at_end_position = HIGH;
    perfusion.set_end_position(at_end_position);
 } else {
  at_end_position = digitalRead(BUTTON_PIN);
  perfusion.set_end_position(at_end_position);
  if (perfusion.get_end_position() == HIGH) {
    perfusion.end_perfusion();
  }
  }
 
}

void CommandParser(String inputString, String *Commands) {
	int index = 0;

	while (inputString.length() > 0 && index < maxCommands) {
		int delimiterIndex = inputString.indexOf(delimiter);
		if (delimiterIndex == -1) {
			Commands[index++] = inputString;
			break;
		} else {
			Commands[index++] = inputString.substring(0, delimiterIndex);
			inputString = inputString.substring(delimiterIndex + 1);
		}
	}
}


void Status(){
	// perfusion.get_motor_speed() will be replaced by flow rate.
	Serial.println("<"+ String(perfusion.get_state()) + ", " + String(valve_status) +", "+ result + ", " + perfusion.get_current_pressure()+ ", "+ perfusion.get_target_pressure() + ", "+ String(rpm,4) +">");
}


void bme_setup(){
  bme.begin();
  // Set up oversampling and filter initialization
  bme.setTemperatureOversampling(BME680_OS_8X);
  bme.setHumidityOversampling(BME680_OS_2X);
  bme.setPressureOversampling(BME680_OS_4X);
  bme.setIIRFilterSize(BME680_FILTER_SIZE_3);
  bme.setGasHeater(320, 150); // 320*C for 150 ms
}


String ReadTemperatureHumidity() {
  float humidity, temperature, pressure;
  uint32_t gasRes;  // gas resistance in Ω

  if (!bme.performReading()) {
    // failed read
    return String("0, 0, 0, 0, 0");
  }

  // Sensor readings
  humidity    = bme.humidity;                          // % RH
  temperature = bme.temperature;                       // °C
  pressure    = (bme.pressure * 0.7500638) / 100.0;    // mmHg
  gasRes      = bme.gas_resistance;                    // Ω

  // 1. Gas score (0–75)
  const float R_min = 50.0;        // Ω (very polluted)
  const float R_max = 50000.0;     // Ω (clean air)
  float gas_score = (R_max - gasRes) / (R_max - R_min) * 75.0;
  gas_score = constrain(gas_score, 0.0, 75.0);

  // 2. Humidity score (0–25)
  float hum_score;
  if (humidity < 40.0) {
    hum_score = (40.0 - humidity) * (25.0 / 40.0);
  } else {
    hum_score = (humidity - 40.0) * (25.0 / 60.0);
  }
  hum_score = constrain(hum_score, 0.0, 25.0);

  // 3. Combine into IAQ (0–500)
  float raw_iaq   = gas_score + hum_score;   // 0–100%
  float IAQ_index = raw_iaq * 5.0;           // scale to 0–500

  // Build CSV string: humidity, temperature, pressure, gas (kΩ), IAQ
  String Readings = 
    String(humidity, 1) + ", " +
    String(temperature, 1) + ", " +
    String(pressure, 1) + ", " +
    String(IAQ_index, 0);

  return Readings;
}


/*

float averageDelta(float newSample) {
  // 1) Insert newSample into our rolling buffer
  if (sampleCount < MAX_SAMPLES) {
    samples[sampleCount++] = newSample;
  } else {
    // shift left, drop samples[0]
    for (uint8_t i = 0; i < MAX_SAMPLES - 1; i++) {
      samples[i] = samples[i + 1];
    }
    samples[MAX_SAMPLES - 1] = newSample;
  }

  // 2) If we don't yet have at least two samples, no delta to compute
  if (sampleCount < 2) {
    return 0.0;
  }

  // 3) Sum up differences between consecutive samples
  float sumDeltas = 0.0;
  uint8_t delCount = sampleCount - 1;
  for (uint8_t i = 0; i < delCount; i++) {
    sumDeltas += (samples[i + 1] - samples[i]);
  }

  // 4) Return average difference
  return sumDeltas / delCount;
}
*/

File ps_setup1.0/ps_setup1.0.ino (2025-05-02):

// Include necessary libraries for LCD, DHT sensor, and BME680 sensor
#include <LiquidCrystal_I2C.h>;
#include <Wire.h>;
#include "DHT.h" ;
#include <seeed_bme680.h> ;

// LCD setup
LiquidCrystal_I2C lcd (0x27,20,4); // Set the LCD address to 0x27 for a 20 chars and 4 line display

// DHT22 sensor setup
#define DHTPIN 2              // Define the pin where the DHT22 sensor is connected
#define DHTTYPE DHT22         // Specify the DHT sensor type
DHT dht(DHTPIN, DHTTYPE);

// BME680 sensor setup
#define BME_SCK 13
#define BME_MISO 12
#define BME_MOSI 11
#define BME_CS 10
#define IIC_ADDR uint8_t(0x76)
Seeed_BME680 bme680(IIC_ADDR); /* IIC PROTOCOL */ // Initialize BME680 sensor with I2C protocol

// Initialize variables for pressure sensor
const int sensorPin1 = A0;    // Analog pin for pressure sensor
int sensorValue1 = 0;         // Variable to store raw sensor reading
int low = 0;                  // low pressure in cmH2O
int high = 0;                 // high pressure in cmH2O
int rawLow = 0;               // low raw sensor reading
int rawHigh = 0;              // high raw sensor reading

void setup() {
 Serial.begin(9600);          // Initialize serial communication
 dht.begin();                 // Initialize DHT sensor

 // Set calibration values for pressure sensor
 high = 10 ;
 low = 5 ;
 rawLow = 46;
 rawHigh = 96;
 

 // Initialize LCD
 lcd.init();
 lcd.backlight();

 // Set LCD labels
 lcd.setCursor(0,0);
 lcd.print("raw:");     // Raw sensor value
 
 lcd.setCursor(10,0);
 lcd.print("lraw:");     // low raw sensor reading 
 
 lcd.setCursor(0,1);
 lcd.print("tDHT:");     // Temperature from DHT
 lcd.setCursor(9,1);
 lcd.write(223); 
 lcd.print("C"); 

 lcd.setCursor(12,1);
 lcd.print("hDHT:");     // Humidity from DHT
 lcd.setCursor(19,1);
 lcd.print("%"); 
 
 lcd.setCursor(0,2);
 lcd.print ("p Cornea:");    // liquid pressure Cornea
 lcd.setCursor(16,2);
 lcd.print ("mmHg");

 lcd.setCursor(0,3);
 lcd.print ("airp BME:");    // air Pressure
 lcd.setCursor(16,3);
 lcd.print ("kPa"); 
 
 // Initialize BME680 sensor
  while (!bme680.init()) {
    Serial.println("bme680 init failed ! can't find device!");
    delay(10000);
  }
}

void loop() {

  // Read pressure Sensor
  sensorValue1 = analogRead(sensorPin1);

  // Calculate pressure in cmH2O
  float numerator = high - low;
  float denominator = rawHigh - rawLow;
  float m = numerator / denominator;
  float b = low - m * rawLow ;
  float pressure = m * sensorValue1 + b; // Pressure in cmH2O
  float p = pressure * 0.73553888361413; // Convert pressure to mmHg

  // Read temperature and humidity from DHT22
  float h = dht.readHumidity();
  int humidity = round(h);               // Round humidity to nearest integer
  float t = dht.readTemperature();
  char tempString[6];
  dtostrf(t, 4, 1, tempString);          // Convert temperature to string with 1 decimal place

  // Check for sensor reading failures
  if (isnan(h) || isnan(t)) {
    Serial.println("Failed to read from DHT sensor!");
    return;
  }

  // Read BME680 sensor data
  if (bme680.read_sensor_data()) {
    Serial.println("Failed to perform reading from BME680 sensor!");
    return;
  }

  // Store BME680 sensor readings
  float BMEt = (bme680.sensor_result_value.temperature);
  float BMEh = (bme680.sensor_result_value.humidity);
  float BMEp = (bme680.sensor_result_value.pressure);
  float BMEg = (bme680.sensor_result_value.gas);

  // Print measurements to serial monitor 
  String values = String(rawLow) + ", " + 
                  String(sensorValue1) + ", " +  
                  String(p) + ", " +
                  String(t) + ", " +  
                  String(h) + ", " +
                  String(BMEt) + ", " +
                  String(BMEh) + ", " +
                  String(BMEp) + ", " +
                  String(BMEg);
                  
  Serial.println(values);
  
  // Print measurements to LCD
  lcd.setCursor(4,0);
  lcd.print(sensorValue1);
  lcd.setCursor(16,0);
  lcd.print (rawLow);
  
  lcd.setCursor(5,1);
  lcd.print(tempString);
  lcd.setCursor(17,1);
  lcd.print(humidity);

  lcd.setCursor(10,2);
  lcd.print(p);

  lcd.setCursor(10,3);
  lcd.print(BMEp/ 1000.0);

  // Wait before taking the next measurement
  delay(500);
}

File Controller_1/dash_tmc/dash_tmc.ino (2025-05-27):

#include <MobaTools.h>

#include <Adafruit_Sensor.h>
#include <DHT.h>
#include <DHT_U.h>

// —– Configuration of sensor —–
#define DHTPIN     2     // Digital pin connected to the DATA line
#define DHTTYPE    DHT22 // DHT 22 (AM2302), AM2321


const byte stepPin = 8;
const byte dirPin = 9;
const int ENABLE_PIN = 10;

const int motorStepsPerRev = 200; // Full steps per revolution
const int microsteps = 64;        // Microstepping setting (e.g., 16 for 1/16 microstepping)
const int stepsPerRev = motorStepsPerRev * microsteps;

MoToStepper stepper(stepsPerRev, STEPDIR);

#define Relay 5

// commands for arduino to operate. The structure is as follows: 1. Stepper motor, 2. Relay,
//String commands[] = {"STOP_MOTOR", "OFF"};
String inputString = "";
const char delimiter = ',';
const int maxCommands = 2;
String Commands[maxCommands] = {"STOP_MOTOR", "OFF",};

bool connected = 1;

// Create sensor object
DHT dht(DHTPIN, DHTTYPE);
String TempHumid[3];

void setup() {

    stepper.attach(stepPin, dirPin);
    //stepper.attachEnable(enablePin, 10, LOW); // 10ms delay, LOW to enable
    pinMode(ENABLE_PIN, OUTPUT);
    digitalWrite(ENABLE_PIN, LOW); // Enable the driver (active-low)
    stepper.setSpeed(1);                     // Speed in RPM
    stepper.setRampLen(50);                   // Ramp length in steps
    stepper.setZero();                        // Set current position as zero

    pinMode(Relay, OUTPUT);

    Serial.begin(115200);
    //Serial.setTimeout(500);

    Serial.println("<OK>");

    dht.begin();
}
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

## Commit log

2025-05-01 Adding files via upload from OneDrive
    Setting up the repository
    [Materialliste.xlsx]
2025-05-02 These files connect arduino with raspberry pi via usb cable
2025-05-06 3D design files
    coupler, rod, stepper,syringe, etc
    [Ecrou M8.STEP]
2025-05-06 3D files
    stepper, syringe, coupler, etc
    [Coupler 6.35-8mm Without Screw.STEP, LM8UU 8mm Linear Bearing.stl, Syringe+20ml+XL+-+21x121mm.f3d]
2025-05-06 3D rod
    Threaded rod
2025-05-12 New files for motor driver added.
2025-05-12 New 3D files added to the repository. The files are ready for 3D printing and include the following formats: .ipt, .step, and .stl. The files are as follows: - Arduino base v12 - Barrel v11 - NemaMou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
    [Arduino base v12.ipt, Arduino base v12.step, Arduino base v12.stl, Barrel v11.ipt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]
2025-05-16 3D files and motor driver code Version 2 of the 3D files and motor driver code with accelstepper library is added.
    [Barrel 10ml v6.ipt, Barrel_Body.stl, Barrel_head.stl, NemaMount 2 v3.stl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]
2025-05-20 Added dashboard.py Added control panel for the stepper motor control with a GUI, it has three buttons to control the motor: run clockwise, run counterclockwise, and stop. It also displays the current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
2025-05-20 Added multiple drivers and removed unused files. Changed button style to be more consistent with the rest of the code. Removed extra files from the repository.
    [Coupler 6.35-8mm Without Screw.STEP, Ecrou M8.STEP, LM8UU 8mm Linear Bearing.stl, Syringe+20ml+XL+-+21x121mm.f3d]
2025-05-21 Valve Control added. The following changes were made: - Added a new function to control the valve. - Integrated the valve control logic into the main loop. - Added a new button to the dashboard for m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
2025-05-22 Added New_connection.py and modified dashboard.py Added new experimental file named New_connection.py for testing new connection methods. Inserted some code in dashboard.py to test the new connection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
2025-05-27 Added Temperature and Humidity Sensor to Arduino.
2025-05-28 Added classes to refactor code for Py and Arduino. Added save_data.py to save data into sqlite database. Added Perfusion class to handle perfusion logic. Added ReadTemperatureHumidity class to handle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
2025-06-03 Added new features to the Controller and Dashboard The Dashboard now set flow_rate in ml/min with minimum value of 1.7 ml/min. The Controller now operates on step per second instead of rpm and a new 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
2025-06-04 Model Sketch has been added A new model sketch has been created and added to the repository using Fritzing.
    [Sketch.fzz]
2025-06-04 Added encoder in sketch
    [Sketch.fzz]
2025-06-05 Added config.h, IR sensor and removed unused files config.h contains all the configuration parameters for the project. IR sensor is used to detect the position of the syringe pump at the end of the p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
2025-06-11 Added venv for raspberry Pi.
2025-06-12 Added databases folder to save new db files. Added functionality to save data every time a perfusion is started. The data is saved accrording to the current date and time. Minor bug fixes in showing 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
2025-06-16 Added AS5048A, updated Controller and Dashboard
    Added AS5048A library for angle sensing, updated Controller to integrate pressure sensing, and made changes to Dashboard for pressure sensor calibration.
2025-06-24 Added 3D files and AS5048A library Added 3D files for AS5048A mount and magnet holder, along with the AS5048A library files.
    [AS5048A_mount v1.ipt, AS5048A_mount v1.stl, Magnet_holder v0.ipt, Magnet_holder v1.stl]
2025-06-24 Added 3D files and AS5048A library Added new Barrel 10ml file with holder for IR button. Added AS5048A library for rotary encoder support to the Controller file. Made changes to set motor based on AS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
    [Barrel 10ml with IR Button v2.ipt, Barrel 10ml with IR Button v2.stl]
2025-06-24 Added csv.py and run scripts for Pi and Windows Added csv.py file to database file into a CSV format. Added run scripts for Raspberry Pi and Windows to execute the csv.py and dashboard.py script.
2025-06-25 Added pressure sensor calibration to Controller Added pressure sensor calibration functionality to the Controller code. Fixed minor bugs in the Dashboard.
2025-06-26 Added new functions to Controller and bug fixes Added speed_in_rpm to Controller, moved pressure functions to new Pressure header file Fixed bug with time in save_data.py converted speed to absolute 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
2025-06-27 Modified Magnet_holder, bug fixes in dashboard.py
    [Magnet_holder v2.ipt, Magnet_holder v2.stl]
2025-07-03 New function added to measure motor speed
2025-07-11 Code reformatted and delay replaced. Reformatted the code to read all sensor data at the beginning of the loop. Replaced delay(1000) with if condition to check if the loop has run for at least 1000 m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
2025-07-11 New button to toggle valve state This commit adds a new button to the dashboard that allows users to toggle the valve state during IDLE mode.
2025-07-11 Minor bug fixes in Toggle Valve Button.
2025-07-14 New libraries for stepper motor and AS5048A added. Tested in new libraries and added formula for accurate flow rate calculation.
    [Formulas.xlsx]
2025-07-15 Added AS5048A check program and RMP Formula New check program for AS5048A checks the distance between AS5048A and the magnet. RPM formula converts the RPM to the Microstepping period.
    [Formulas.xlsx]
2025-07-16 Changed Perfusion library and minor bug fixes
    [Formulas.xlsx]
2025-07-21 Modified print statements for loading time.
2025-07-21 Minor bug fixes
    [Formulas.xlsx]
2025-07-22 Improved the measurements of the 3D models.
    [AS5048A_mount v2.ipt, AS5048A_mount v2.stl, Barrel 10ml with IR Button v3.ipt, Barrel 10ml with IR Button v3.stl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]
2025-07-24 New file added for BME680 Sensor Reading
2025-07-29 Changes made in sensor data handling and dashboard New bme680 sensor is implemented and data structure is updated accordingly.
2025-07-30 New Excel sheet for measurements added
    [Measurements.xlsx]
2025-07-31 Calculations changed for TMC controller
    [Formulas.xlsx, Measurements.xlsx]
2025-07-31 More Measurements and formulas added.
    [Formulas.xlsx, Measurements.xlsx]
2025-08-01 New reverse button functionality in the dashboard Reverse button added to the dashboard for adjusting syringe position. New Measurements added.
    [Formulas.xlsx, Measurements.xlsx]
2025-08-06 Changed valve state reading functionality
    [Measurements.xlsx]
2025-08-07 Changed the valve state reading
2025-08-08 New UI added to Dashboard_2
    [Measurements.xlsx]
2025-08-11 Minor bug fixes and new Measurements added.
    [Measurements.xlsx]
2025-08-13 New 3D files and Measurements added.
    [Measurements.xlsx, Plunger v15.ipt, Plunger v15.stl]
2025-08-14 Added Measurements and updated TMC controller
    [Measurements.xlsx]
2025-08-19 New pressure sensor added to the controller
    [Measurements.xlsx]
2025-08-21 Add a measurement and changed speed in TMC.cpp
    [Measurements.xlsx]
2025-08-26 Added Measurements and minor bug fixes in Arduino
    [Measurements.xlsx]
2025-08-29 Changed speed parameter and added a Measurement.
    [Measurements.xlsx]
2025-09-04 New Measurements added
    [Measurements.xlsx]
2025-09-16 New Measurements and 3D files for Gearbox added
    [MGL17-G20_Holder v1.ipt, MGL17-G20_Holder v1.stl, Measurements.xlsx, Perfusion_Shield v35.f3z]
2025-09-22 Output file name changed for CSV files
    [Measurements.xlsx]
2025-09-23 Speed parameter and valve safety threshold changed
2025-09-23 Time parameter changed for AS5048A Now time to measure the speed is set dynamically according to the speed of the motor
2025-09-26 New Measurements added and formula improved
    [Formulas.xlsx, Measurements.xlsx]
2025-10-15 New PCB design files added for perfusion shield
    [Perfusion_Shield.kicad_pcb, Perfusion_Shield.kicad_sch, Perfusion_Shield.step]
2025-10-17 New Measurements added to the Excel file
    [Measurements.xlsx]
2025-10-20 Perfusion data file
    [perfusion_20251001_121923.csv]
2025-11-03 Deleted temporary files
    [Formulas.xlsx, Measurements.xlsx, perfusion_20251001_121923.csv]
2025-11-03 Renamed folder removed empty folders.
    [Materialliste.xlsx]
2025-12-04 New 3D files for Arduino Housing design added
    [Arduino_Housing Top v2.stl, Arduino_Housing Top.ipt, Arduino_Housing v5.ipt, Arduino_Housing v5.stl]
